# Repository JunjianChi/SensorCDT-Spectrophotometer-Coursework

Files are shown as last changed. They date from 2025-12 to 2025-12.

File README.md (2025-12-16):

# SensorCDT Spectrophotometer Cousework
Low-cost Spectrophotometer for Juice Classification
===================================================================================

In this work, we present a 3D-printed reproducible spectrophotometer system integrating an Arduino MCU with AS7343 spectral sensor. 12-channel raw measurements are pre-processed and used to train machine learning models for juice type and concentration classification. Based on the performance on an independent test set, the best two models achieve a test accuracy of 100% for juice type classification, and 82.35% for concentration classification.

<p align="center">
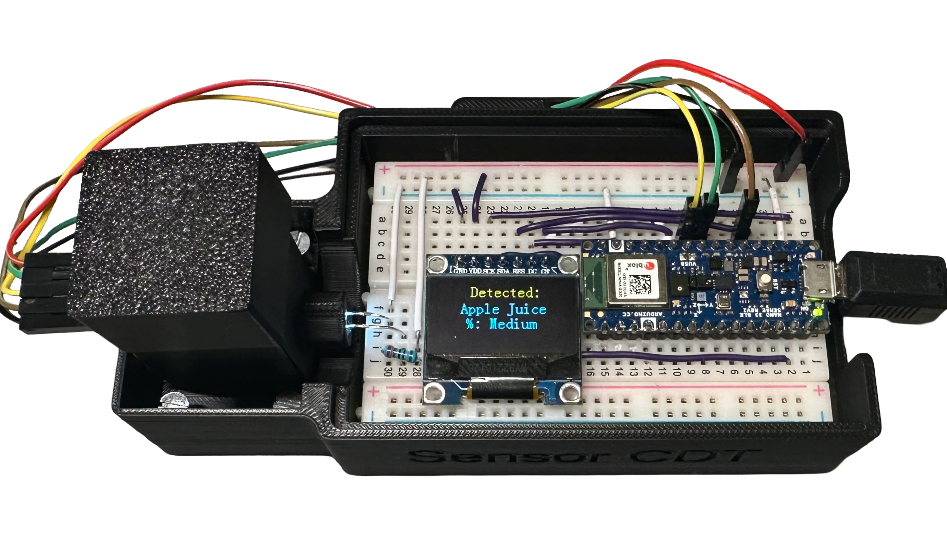
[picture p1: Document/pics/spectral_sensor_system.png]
  
</p>

Example Readout:

<p align="center">
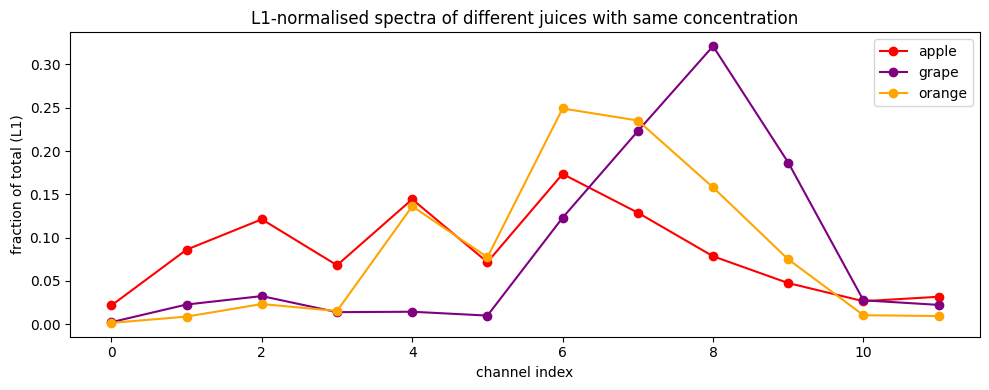
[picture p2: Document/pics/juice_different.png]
  
</p>

Mechanical Assembly
-------------------

3D assembly reference image:

<p align="center">
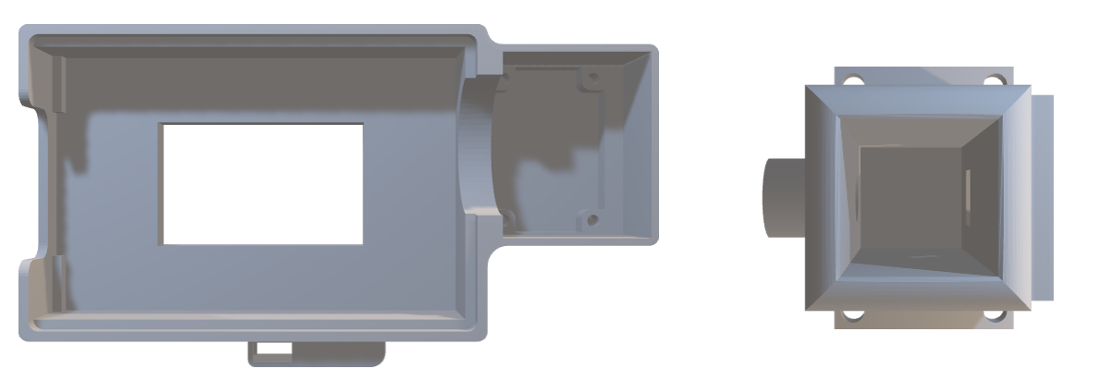
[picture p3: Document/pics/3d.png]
  
</p>

The mechanical enclosure consists of three 3D-printed components located in the
STL folder.

Assembly steps:
1. Print all three STL files from the STL folder.
2. Use PLA filament.
3. Suggested print settings:
   - Layer height: 0.2 mm
   - Infill: 20–30%
   - Supports: not required
4. Assemble the enclosure using the screws listed below.

### Required Fasteners

- 4 × M3 screws
- 2 × M2 screws

Electrical Connections 
-------------------------------

### Pinout (Arduino Nano 33 BLE Sense Rev2)

| Module | Signal | Arduino Pin |
|-------|--------|-------------|
| OLED (SSD1306) | SCK | D13 |
| OLED (SSD1306) | SDA | D11 |
| OLED (SSD1306) | RES | A0 |
| OLED (SSD1306) | DC  | A7 |
| OLED (SSD1306) | CS  | A6 |
| AS7343 | SDA | A4 |
| AS7343 | SCL | A5 |
| AS7343 | INT | A1 |

Ensure all modules share a common ground (GND) and correct supply voltage 3.3V.

Firmware Setup
--------------

The firmware is developed using PlatformIO with Visual Studio Code.

Requirements:
- Visual Studio Code
- PlatformIO extension
- Arduino Nano 33 BLE Sense Rev2

Setup steps:
1. Open the Firmware folder in Visual Studio Code.
2. Ensure PlatformIO detects the correct board.
3. Install required libraries specified in platformio.ini.
4. Build and upload the firmware.
5. Open the serial monitor at 115200 baud.

PC-Side Software
----------------

Python scripts for data acquisition, machine learning inference, and evaluation are located in the PC folder.

Install required dependencies using:

```
pip install -r requirements.txt
```

Bill of Materials (BOM)
----------------------

No | Item        | Description                                   | Price (£) | Qty | Total (£) | Source
---|-------------|-----------------------------------------------|-----------|-----|-----------|-------------------------
1  | OLED        | 0.96” SSD1306 OLED display module              | 4.00      | 1   | 4.00      | https://www.adafruit.com
2  | Arduino MCU | Arduino Nano 33 BLE Sense Rev2                 | 37.81     | 1   | 37.81     | https://store.arduino.cc
3  | AS7343      | Pimoroni AS7343 multi-spectral sensor          | 18.90     | 1   | 18.90     | https://shop.pimoroni.com
4  | PLA         | PLA filament, 1.75 mm (50 g)                   | 1.00      | 1   | 1.00      | https://www.amazon.co.uk
5  | White LED   | White 5 mm LED                                 | 0.27      | 1   | 0.27      | https://www.amazon.co.uk
6  | Resistor    | 220 Ω resistor                                 | 0.04      | 1   | 0.04      | https://www.amazon.co.uk
7  | Wire        | Jumper wires                                   | 0.07      | 5   | 0.35      | https://www.amazon.co.uk
8  | Breadboard  | Solderless breadboard                          | 4.95      | 1   | 4.95      | https://www.amazon.co.uk

Total cost: £67.32

Troubleshooting Guide
---------------------

No serial output:
- Check baud rate is set to 115200.
- Verify USB cable supports data transfer.
- Confirm correct COM/USB port is selected.

OLED display not working:
- Verify SPI pin connections.
- Check OLED library compatibility.

Spectral sensor not detected:
- Verify I2C wiring (SDA/SCL).
- Check sensor address and power supply.

Inconsistent readings:
- Minimize ambient light interference.

License
-------

This project is released under the MIT License.

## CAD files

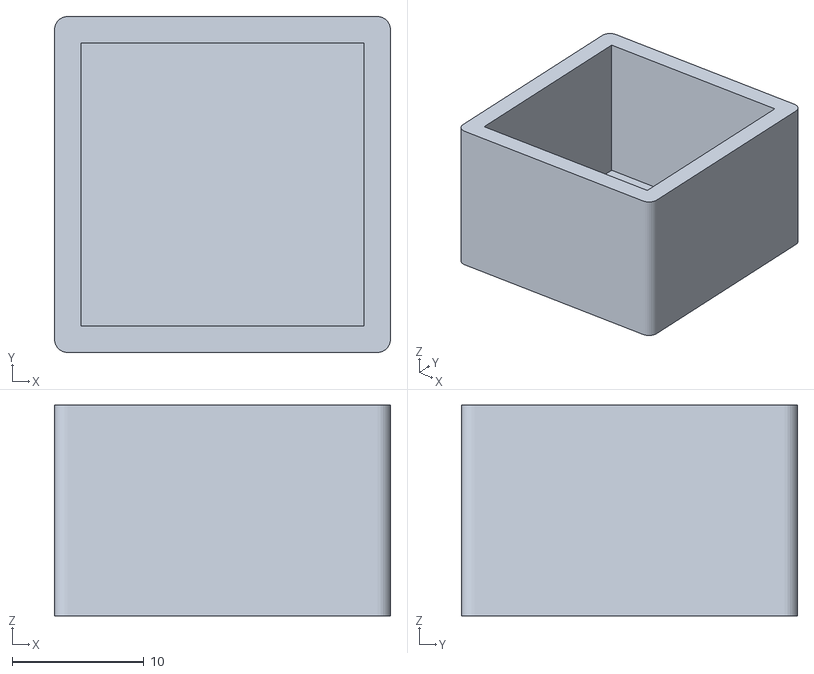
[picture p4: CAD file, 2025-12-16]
STL/Cuvette_lid.stl
25.5 x 25.5 x 16.0

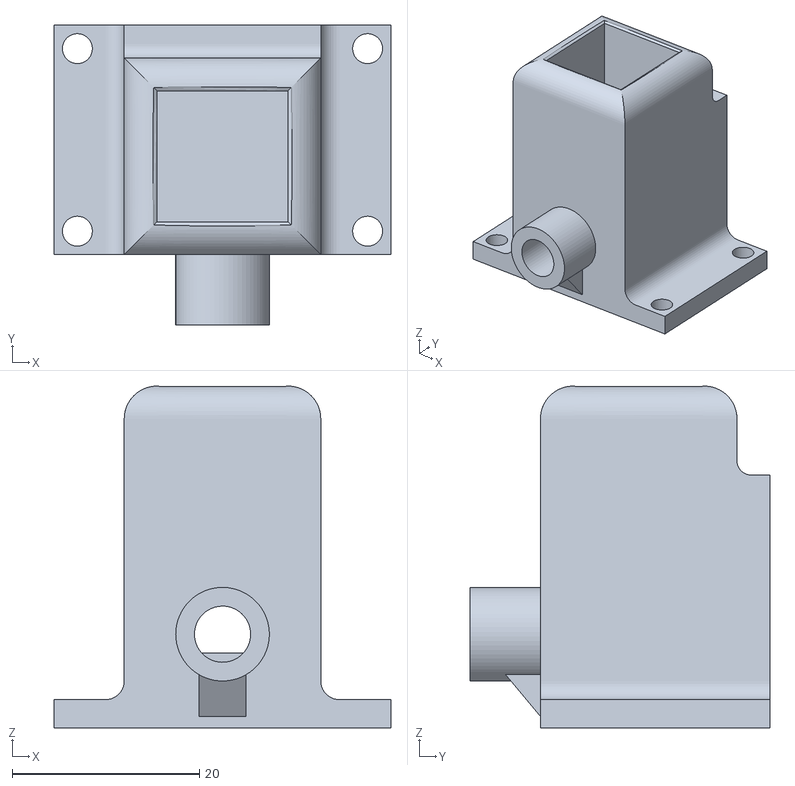
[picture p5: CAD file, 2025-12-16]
STL/Cuvette_holder.stl
36.0 x 32.0 x 36.5

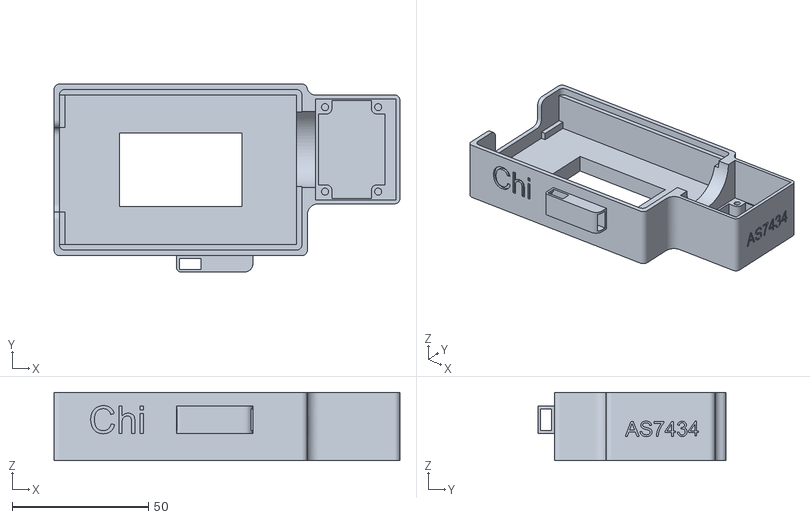
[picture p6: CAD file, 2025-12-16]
STL/Bottom_case.stl
127.0 x 69.0 x 25.0

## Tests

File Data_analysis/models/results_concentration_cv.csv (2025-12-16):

model | preprocess | folds | seed | test_size | mean_accuracy | std_accuracy | mean_macro_f1 | std_macro_f1 | n_train | n_test | n_all
random forest | mean | 5 | 42 | 0.2 | 0.732051282051282 | 0.11238260000415962 | 0.7310582010582011 | 0.11309399733222039 | 64 | 17 | 81
gradient boosting | mean | 5 | 42 | 0.2 | 0.4833333333333333 | 0.08383478320139391 | 0.4252188552188552 | 0.12125431364432379 | 64 | 17 | 81
svm_lin | mean | 5 | 42 | 0.2 | 0.4051282051282052 | 0.08488689926793255 | 0.3762097162097162 | 0.07970300527113235 | 64 | 17 | 81
svm_rbf | mean | 5 | 42 | 0.2 | 0.40512820512820513 | 0.04971979340939826 | 0.35491101491101495 | 0.06232177245092732 | 64 | 17 | 81
logistic regression | mean | 5 | 42 | 0.2 | 0.3282051282051282 | 0.05710527551620535 | 0.2692063492063492 | 0.06685988628508067 | 64 | 17 | 81

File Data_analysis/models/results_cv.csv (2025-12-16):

model | preprocess | folds | seed | test_size | mean_accuracy | std_accuracy | mean_macro_f1 | std_macro_f1 | n_train | n_test | n_all
random forest | l1 | 5 | 42 | 0.2 | 1.0 | 0.0 | 1.0 | 0.0 | 64 | 17 | 81
gradient boosting | l1 | 5 | 42 | 0.2 | 0.9846153846153847 | 0.03076923076923075 | 0.9851851851851852 | 0.02962962962962963 | 64 | 17 | 81
svm_rbf | l1 | 5 | 42 | 0.2 | 0.9692307692307693 | 0.03768445758127964 | 0.9696007696007696 | 0.03725118154716261 | 64 | 17 | 81
svm_lin | l1 | 5 | 42 | 0.2 | 0.8615384615384617 | 0.08970695222838923 | 0.8615658415658416 | 0.08786527383762925 | 64 | 17 | 81
logistic regression | l1 | 5 | 42 | 0.2 | 0.7346153846153847 | 0.12427303401079627 | 0.7119265919265919 | 0.1340426764030837 | 64 | 17 | 81

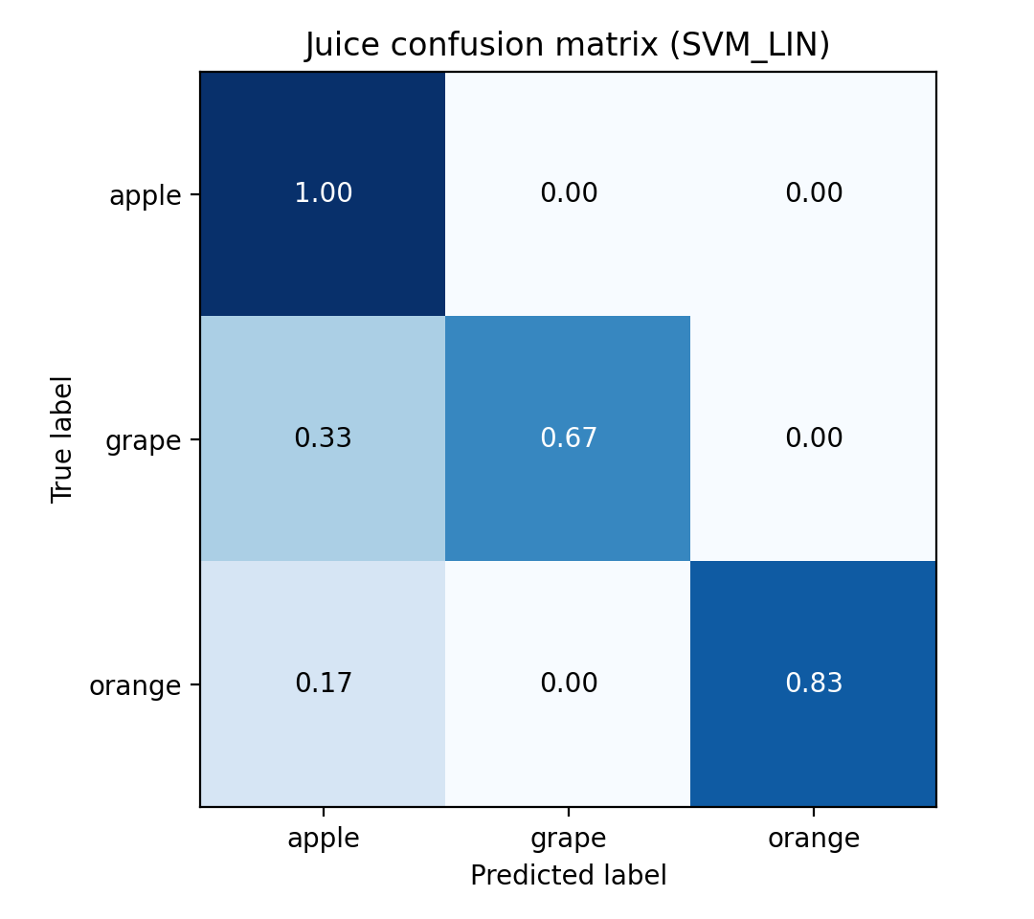
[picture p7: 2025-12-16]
Data_analysis/models/figures_juice_test/cm_svm_lin_norm.png

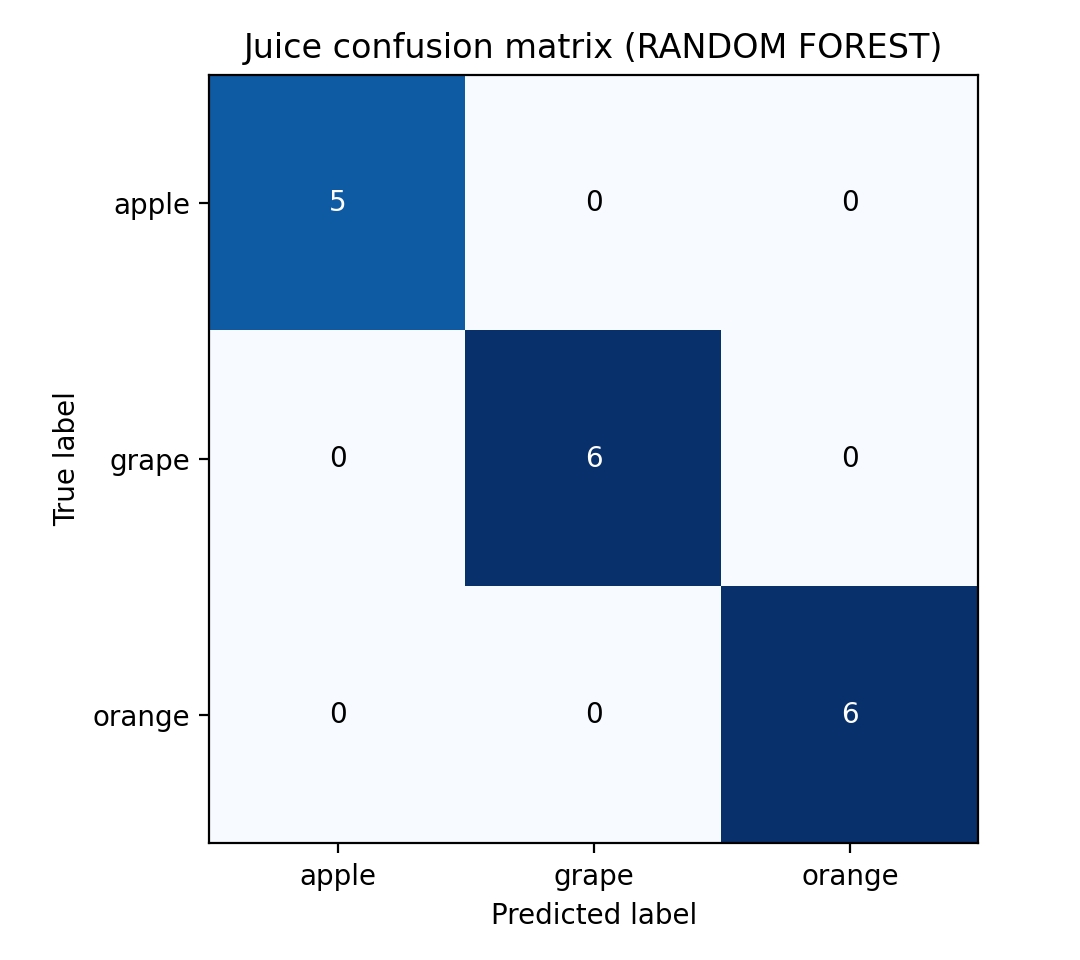
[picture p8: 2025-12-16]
Data_analysis/models/figures_juice_test/cm_random_forest.png

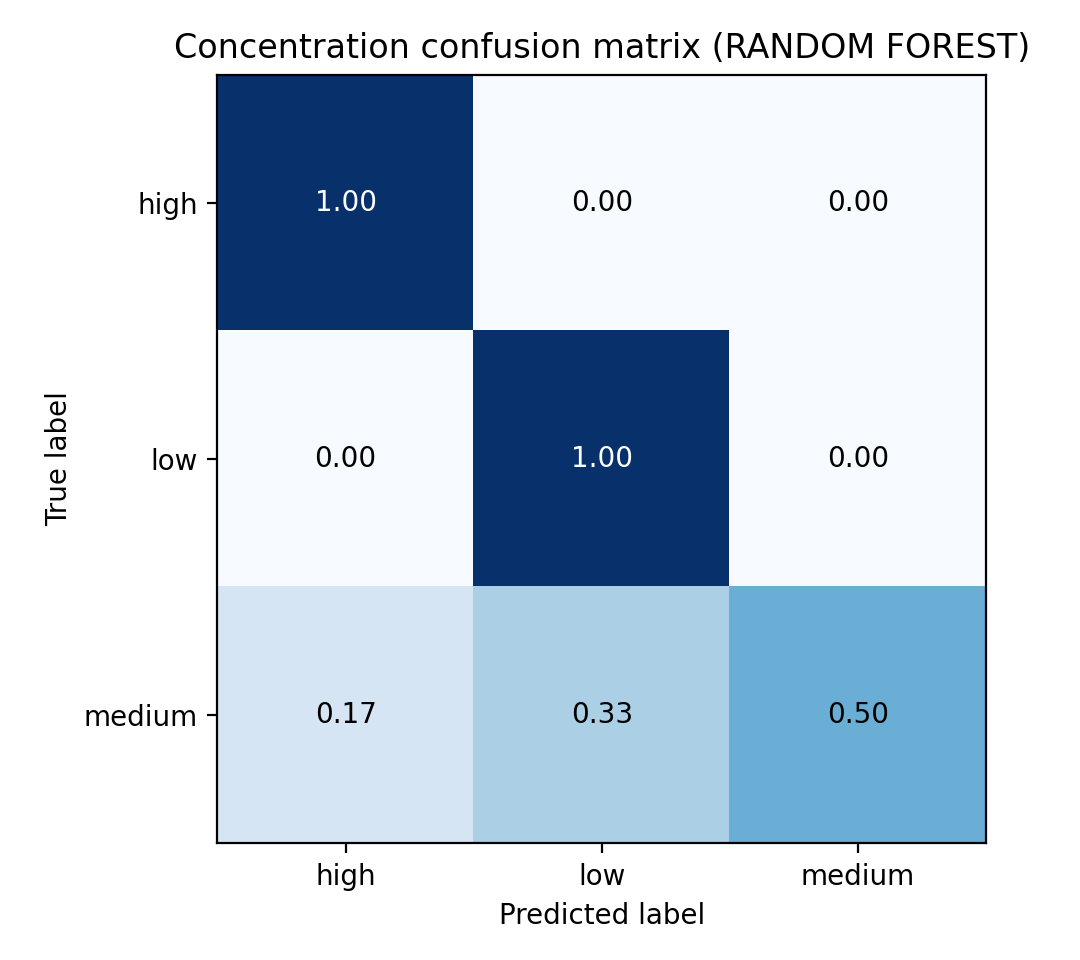
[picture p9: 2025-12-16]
Data_analysis/models/figures_concentration_test/cm_random_forest_norm.png

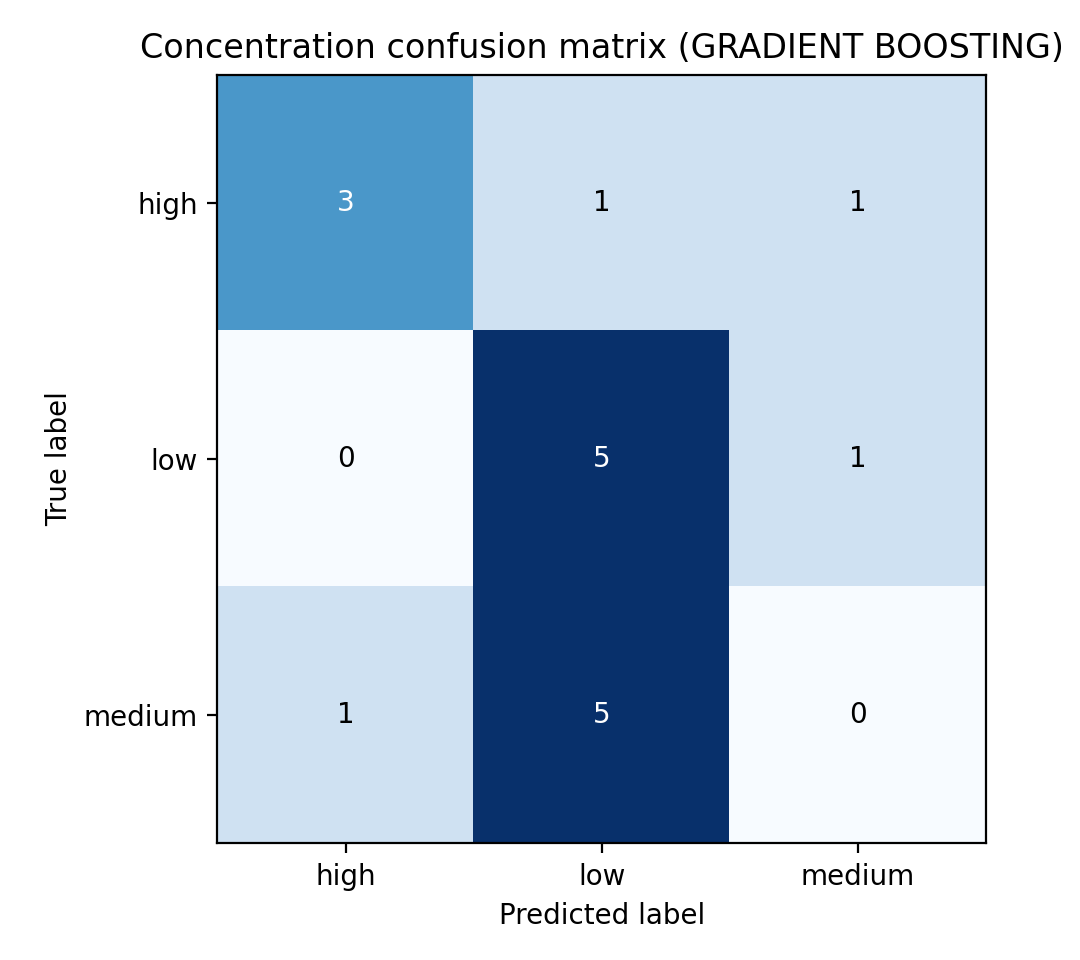
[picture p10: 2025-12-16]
Data_analysis/models/figures_concentration_test/cm_gradient_boosting.png

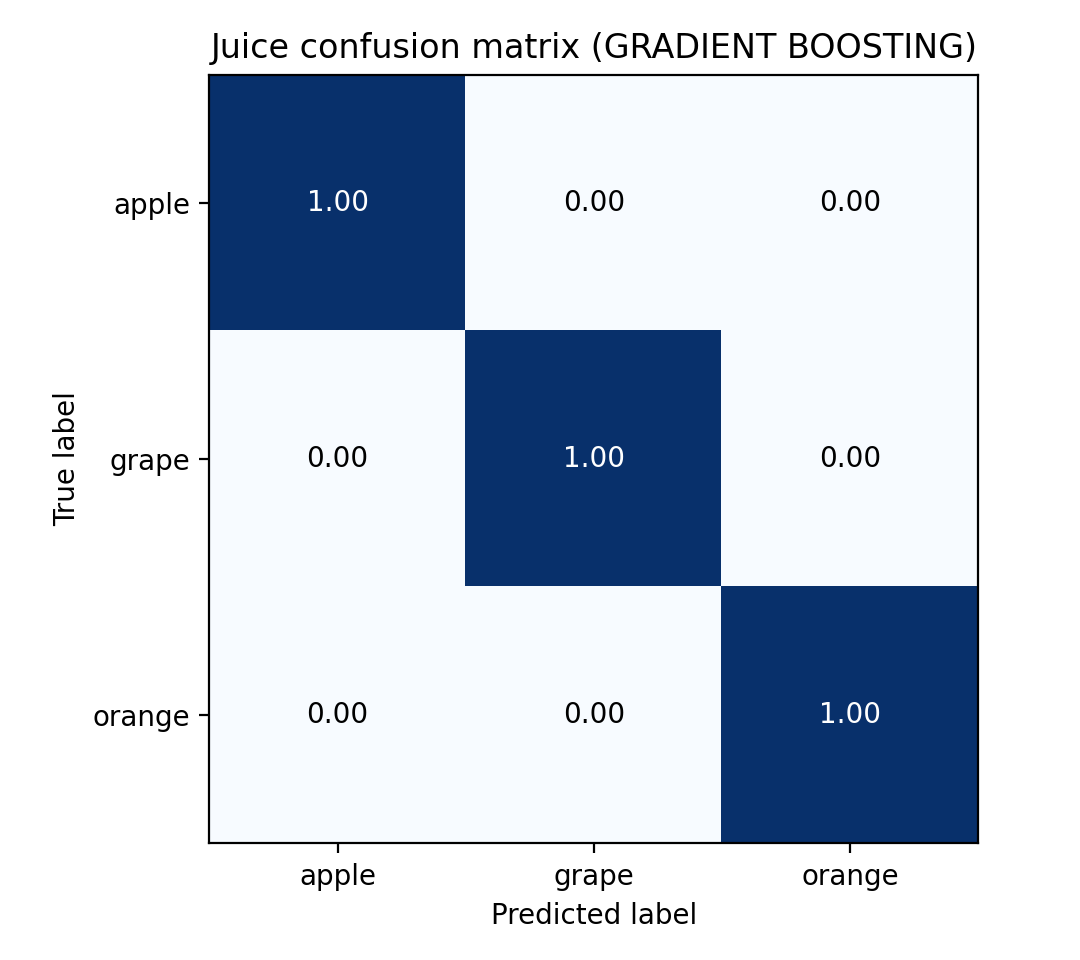
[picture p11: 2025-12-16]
Data_analysis/models/figures_juice_test/cm_gradient_boosting_norm.png

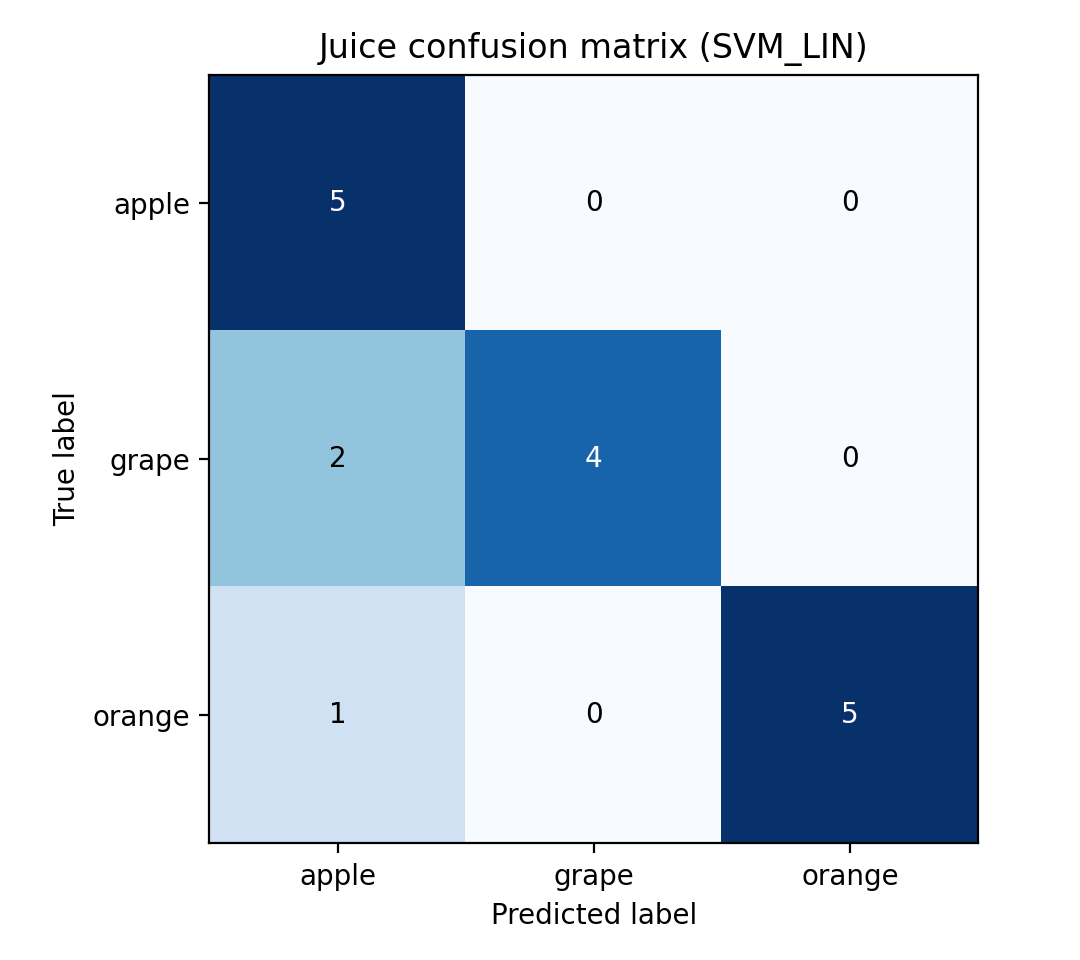
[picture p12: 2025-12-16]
Data_analysis/models/figures_juice_test/cm_svm_lin.png
